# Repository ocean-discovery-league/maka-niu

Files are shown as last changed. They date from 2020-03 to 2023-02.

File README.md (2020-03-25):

# maka-niu

"Maka" - Eye, "Niu" - Coconut

Maka Niu, aka the "CocoCam,"  is a low-cost oceanographic camera and sensor platform that enables the exploration of undersea environments using a new pressure-tolerant camera housing and an all-natural, locally sourced, biodegradable buoyancy-control device. The coconut (Cocos nucifera ) can float for over 3,000 miles and still remain viable; as such, it makes an excellent organic platform for deploying scientific apparatus.

Maka Niu is a community-driven project that allows local groups to explore and monitor their marine resources. Based around off-the-shelf single-board computers and readily available microprocessors, Maka Niu is inexpensive to produce, easy to program, and simple to use. Designed as an open platform for scientific education and exploration, it will give classrooms and communities the ability to upload video and sensor data into FathomNet, a centralized database where machine learning algorithms assist with classification of marine species, seabed substrate identification, and accumulated time-series sensor data. This data will be publically available, allowing visualization, sharing, and discussion with policy makers from the local to global levels.

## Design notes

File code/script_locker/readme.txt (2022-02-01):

The scripts in this folder need to be copied to the following destinations if those files are outdated. 
This would be the case for fresh operating systems, or if the scripts them selves are revised.

Use sudo cp to get to replace the following files:

(to setup auto start of the main python script along with error dumping)
/etc/rc.local

(to avoid leftover flags from boxing)
/var/www/html/macros/startstopX.sh

(To enable ic2 and spi)
/boot/config.txt

(To give python control of image and video filenames) 
/var/www/html/raspimjpeg

(With new pi zero 2 w, to library error when running python script)
/usr/local/lib/python3.7/dist-packages/adafruit_platformdetect/constants/boards.py

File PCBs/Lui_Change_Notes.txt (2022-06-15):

The CHG pin and the CHEM pin on LTC4007 should be connected to ground to disable timer termination, and to set final charge voltage at 4.1V to avoid OV states. 

BMS
Observations:
-still will cut off charging as it get a little too hot. 
-for a test, TH2 replaced with 10K resistor. This does prevent the heat trighgered stop, but it's probably not something we want unltimately. 
TH2 put back. 
-Root issues is L2 and L3 get too hot. Should study up on inductor efficiency to reduce waste and improve heat dissipation in the PCB with vias and copper planes etc.
-There was confusion about the hall sensing. It all works when the pi and hall are connected together. 
-I think the fact that the pi provides ground to the hall sensor was a bad design choice, but I was short on wires I could use.
-R25 was not soldred properly, fixed and output is now stable off, till cool, and then back on, during overheat shutdown situation. 
-But this temp power loss is not ok if usign wireless charging, only ok with direct power supply. 
-

Changes:
-Cut the SHUT_DOWN_SIG line at the charger IC. It does not pull the line high when charging is not in effect( Should add resistor option to pull up this signal)
-Current limiting resistor set at 0.200ohm, limiting the 15V line to half amp. That measn the 12V line is .625ams, for a charging system running at 7.5W. Sadly this is half of original intent.
-Should improve thermal dissipation.
-Can increase PCB size and cover up all the screw holes. Slighly annoying for assembly, but heat management is more important.
-Make sure R25 is assembled. 
-Cut the TS_EOC line, believing that it was interfering with charging. Does not appear to be the cause
-Looking at scope, connection made and then instanly lost. Perhaps cause is inrush current at the boost circuit. Therefore, changing the inrush controlling cap on the BMS. Much imroved but not perfect. 
-C12 changed from 15nF to 1500nf, which should increse statup time from 1125uS to ~100ms (HEADS UP, BMS# 1 and 3 have 0.22uF caps at C12)
-Thermistor on the BMS replaced with 10K resistor. Charging now works longer, until it crashes but now I think the cause is heat from the bms affectign the wireless receiver circuit. 
-Reducer current consumption further by using .300 ohm R_sense. Now can truly a achive continuos charging, expect after 2 hours the charge timer kicks in.
-Disabled charge timer by shorting CHG pin to gnd
-A bit earlier, changing the charging rate current sense resistor to achieve higher final charge voltage, since I cut off power when we reach 10% of max possible. 
-This worked to raise final voltage to 4.15V, but introduced strange behavior that "locked" charging after one attempt. Resistor return to original 0.1 value. How can I get this to work in both situations
-C19 change to 1uF to increase soft start time. 

-Next: reassemble with thermal separator and reduce current by placing 0.250ohm current limiter, reconnect TS_EOC line
-Great, can now charge continuously. Let's run 1 hour semi open, then one hour fully closed.
-REsearch how to reduce heat in the first place. The inductors I used have pretty high resitance, 0.2 ohms, i can get once with quarter that. So I calcualte heat dessipation to be .2W, and I can bring it down to .05W 
-replaced with new inductors. Some imporvement, but not significant
-Test TS_EOC, am not understanding why this does not act as expected. Reached out to Renesas.
-On charger 1, C12 and C19 now 1uF.

-WARNING: Feb2nd 2021: Way too many BMS boards have only one time charge behavior. What gives? Preboost is fine. 

-Total discharge test: ~24 hours with raspidvid running, wifi on
-Total charge enclosed test: 11 hours when current limiting with 0.3ohm, 5V fan cooling
-Total discharge test: 1:45PM, X hours, wifi off, recording 30 minute videos in succesion. Boxing enabled so may prevent some videos. 
-Total charge enclosed test, 5V fan, .25ohm current limit, new thermal pad with higher pressure sandwich, lower height inductors: Started at 2:45PM. end 11:15. Charger current at start is .72amps

CHARGER BOARD
Notices: 
- New board does not flash any LEDS on power up, indicating a major issue
- Fan is started off the bat, indicating TS not behaving as intended. Noteworthy is that the eval board has TH1 unpopulated, so this coudl easily be the entire problem. NOPE, not that.
- 5V, 3.3, and 1.8 Volt lines provided by the chip are all good and clean, indicating chip is powered and at least partially functional. 
- SIGH. This chip is P9242-RBNDGI8 (colloquially P9242-R3 or RB), and it seems we wanted P9242-RNDGI8 aka(but colloquially P9242-R). Pretty dumb 
- Replaced P9242-R. All good!
- The circuit that control the fan uses a compartor and it's making the opposite decision. inputs flipped.
- Cooling fan adjustements: R17 swapped for 12.1Kohm to reduce fan on threshohold. Works but annoying oscilating behavior.
- added 90K ohm hysterisis resistor. Now very happy with performance, but after some time, would recommend even higher value so that the fan eventually shuts off in idling mode. use 250K
- Consider charging fan power source to 5V rather than 12V for quiter operation. Current cooling seems excessive.  

SYSTEM WIDE
next try to limit current of RX board and pump 9W. Yeah, added a 5.1K ohm R at R22 on the RX board, and power transfer does work now, but still cuts out after a few seconds. (currently removed, put it back))
This shoudl work better now if tested with the BMS with it's own current limiting. 
Main issue i think is distance between coils and alignment issues. Fixed alignment with pins, but the coil distance is I think over 3mm so work next step make sure coil distance is 2.5 to 3mm.

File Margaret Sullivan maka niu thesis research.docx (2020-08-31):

Margaret Sullivan

Thesis Document/ Progress Report

LED module for Maka Niu

After meeting, I have identified three separate components of the project.

1. Geometry of the Light
2. Requirements of Light
3. Circuit Design

Geometry of Light

The desired geometry will heavily depend on the use interviews and input. In order to account for that I created a script in MATLAB to visualize different combinations of variables in order to see what the light covers.

The variables in the geometry are the following

• θ the camera lense angle

• α the LED light projection angle

• φ the angle of the led

• x distance from light to camera

Considerations into the geometry include the ideal range of photography and the width of the lights from the camera. These both will depend on the use cases. The following figures display different combinations. The light projection of the LED is based on the Full Width Half. Minimum (FWHM) value. The beam of light is not as definitive as pictured. The distance between the lower and upper FWHM intersection points and the camera are calculated by

Lower Intersection=x tan⁡(90-φ-α/2 )

Upper Intersection=x tan⁡(90-φ+α/2 )

In these figures, the blue outlines are the edge of the FWHM beam. The camera view is shown in-between the red lines.

Without more user input there is no way to choose the optimal lighting situation. Additionally, different usages may contradict each other in terms of optimal lighting geometry. These must be taken into account when deciding the geometry.

Requirements of Light

In order to determine which LEDs to use and design the module the light necessary must be calculated. The light required will depend on many available such as time of day, depth, and distance. To accommodate these changes another MATLAB Script was written to determine the minimum light for various distance.

The minimum light required for a camera is dependent on make and model. To begin we look at the responsivity of the cameras sensor module. Transforming that information into a light requirement per pixel allows for the calculation of light needed at the object of interest to begin.

Factors that affect the light requirement that will be variable

•Distance of the Object ( y_(dist) ) (assuming it is directly in front of camera)

•Distance of the lights from camera ( x )

•Light attenuation Coefficient ( Kd )

•Emissivity of the Object ( ε )

•The Led Projection angle ( α )

Factors that affect the light requirement that are constant

•Active Pixel Count (3280 x 2464)

•Camera Lens Angle (62.2 degrees) ( θ )

•Absolute Sensitivity Threshold (*NEED THIS*)

•Shutter Speed

•Pixel Size

Starting with the absolute sensitivity threshold we can calculate the total lumens needed for any given factor by the following steps. I created a MATLAB script that follows these calculation and results in the lumens required for the light.

1. *Translate the Absolute Sensitivity Threshold into a useable Unit* Preferably into the Lumens needed per pixel using the Shutter Speed, Pixel Size, and Absolute Sensitivity Threshold.

=#[(lm)/(pix)]

2. Using the Lumens needed for pixel account for the attenuation of light from the object to the lens. Where kd is the attenuation coefficient and the y_(dist) is the distance to the object from the light

Lumens From Object [(lm)/(pix) ]=((# (lm)/(pix) ))/(e^((-kd*y_(dist) )))

3. Accounting for the emissivity of object, calculate the lumens needed per pixel.

Lumens at Object [(lm)/(pix) ]=(((lumens from Object) (lm)/(pix) ))/ε

4. Calculate the Lux at the object using the projection of a single pixel at the distance to the object. Assuming that the pixels cover a square distance, calculating the distance of the arc at the objects’ distance and dividing it by active pixels in that direction gives us the projected area.

arc Length [m]=θ/(360°)2πy_(dist)

area per pixel (m^2)/(pix)=((arc Length)/(wide Pixel #))^2

Lux at Object (lm)/(m^2)=(Lumens at Object [(lm)/(pix) ])/((area per pixel)[(m^2)/(pix)])

5. With the lux at object needed known, we can back track using the surface area of the cone of light provided by the LED. To calculate we must know the distance from the light to the object.

Distance from light [m]=√((x)^2 +(y_(dist) )^2)

6. To calculate the surface area of the light provided by the LED at the distance we must calculate the Solid angle.

∫_0^θ 2π(Rsin(ϕ))Rdϕ=2πR^2 ∫_0^θ sin(ϕ)dϕ

solid angle Ω=2πR^2 (1-cos(θ))

Using a unit sphere so R = 1, the solid angle equation reduces to

Ω=2π(1-cos(θ))

Surface Area [m^2 ]= Ω*(Distance from light )^2

7. To calculate the total lumens at the given distance we can use the Surface area of the light (the spherical cap) at the distance and the needed lux.

Lumens ariving at Object [lm]= Surface area [m^2 ]*lux at Object (lm)/(m^2)

8. Accounting for the light attenuation from the LED to the object we are left with the total lumens needed from the light.

Lumens from light [lm]= (Lumensat Object [lm])/(e^((-kd*Distance From Light)))

This calculation should give us an idea of the lowest number of lumens needed to be produced by the LED given the situation.

Some Key Assumptions made

•Light is evenly distributed within the FWHM

•Attenuation equation works for Lumens

•Pixels cover equal area

•Only use the active pixels

•The object is directly in front of camera

To begin the calculations to determine lumens the amount of light per pixel is necessary. There are many ways or estimating/ determining this number, the below steps show the method in which I estimated it. The data sheet is not complete, so researching similar cameras I was able to come up with an estimate for many necessary components. A detailed study was conducted with the use of the IMX249 sensor (https://www.flir.com/discover/iis/machine-vision/how-to-evaluate-camera-sensitivity/) The IMX249 has some key differences from the Raspberry Pi Camera’s IMX219, but it provides useful details. They differ on pixel size, shutter speed, and total active pixels, but use the same CMOS board and should have similar sensitivity.

The IMX249 absolute sensitivity threshold, meaning the signal is equal to the noise of the sensor is at a light density of 1[ photon/μm^2 ] . Additionally, the saturation light density for the IMX249 is 1200 [ photon/μm^2 ] . The IMX249 has a pixel area size 30 times of that of the IMX219. This results in the IM219 absolute sensitivity threshold to be approximately 30 [ photon/μm^2 ] .

(watts)/(pixel)=[photon Density[(photons)/(μm^2)]][energy of photon[J/(photon)]](area of pixel)

Lumens per pixel =((watts)/(pixel))(LED efficiency)

energy per photon =h*c/λ

The energy of the photons were estimated using blue light, the most prominent light in the water. Where λ is the wavelength of blue light, h is planks constant, and c is the speed of light.

Using the steps listed above to reach the absolute minimum threshold, 39 lumen are required at an object distance of 2 meters with a light FWHM angle of 30. This only reaches the lowest boundary of visibility. For a quality photo I estimate we will want 1/3 of the saturation lighting which puts are light density at approximately 1200 [ photon/μm^2 ] . Using the MATLAB script based off the methodology above this lighting density requires 1550 lumens between the two LED modules.

https://www.flir.com/discover/iis/machine-vision/how-to-evaluate-camera-sensitivity/

-all the absolute sensitivity stuff

https://aggressivegarden.com/ppfd/

https://www.lumigrow.com/learning-center/blogs/par-ppf-ppfd-dli-ppe/

https://www.ncbi.nlm.nih.gov/pmc/articles/PMC4354036/

http://electron6.phys.utk.edu/phys250/modules/module%201/photons.htm

https://www.arducam.com/downloads/modules/RaspberryPi_camera/IMX219DS.PDF

imx 219

https://photo.stackexchange.com/questions/21776/what-is-the-lowest-level-of-luminous-flux-a-camera-can-detect

https://photography.tutsplus.com/articles/a-guide-to-using-consumer-led-bulbs-for-photography-and-video--cms-22708

https://www.dormgrow.com/par/

https://www.britannica.com/science/seawater/Optical-properties

https://study.com/academy/lesson/energy-momentum-of-a-photon-equation-calculations.html

https://www.stemmer-imaging.com/en/knowledge-base/sensitivity/

https://en.wikipedia.org/wiki/Solid_angle

https://www.pveducation.org/pvcdrom/properties-of-sunlight/photon-flux

https://www.pveducation.org/pvcdrom/properties-of-sunlight/spectral-irradiance

http://www.parsource.com/content/light-unit-conversion-table

https://support.pixelink.com/support/solutions/articles/3000034837-how-to-interpret-digital-camera-parameters

https://www.nde-ed.org/EducationResources/CommunityCollege/Radiography/Physics/attenuationCoef.htm

https://www.esf.edu/efb/schulz/Limnology/Light.html

https://www.lumenera.com/blog/understanding-camera-sensitivity-a-look-at-the-numbers

https://www.sciencedirect.com/topics/engineering/luminous-intensity

https://www.waterontheweb.org/under/lakeecology/04_light.html

http://cmore.soest.hawaii.edu/summercourse/2013/documents/2013_lectures/Week2/Day1/5_barone_LectureAgouron2013.pdf

https://www.ledsupply.com/leds/cree-xlamp-xm-l2-leds?gclid=CjwKCAjw9vn4BRBaEiwAh0muDIgXzSZ8uIiwv8MGID8M_GXzRxrjX149hkezV1Zndyf2tEIbTEkI-RoCdfIQAvD_BwE

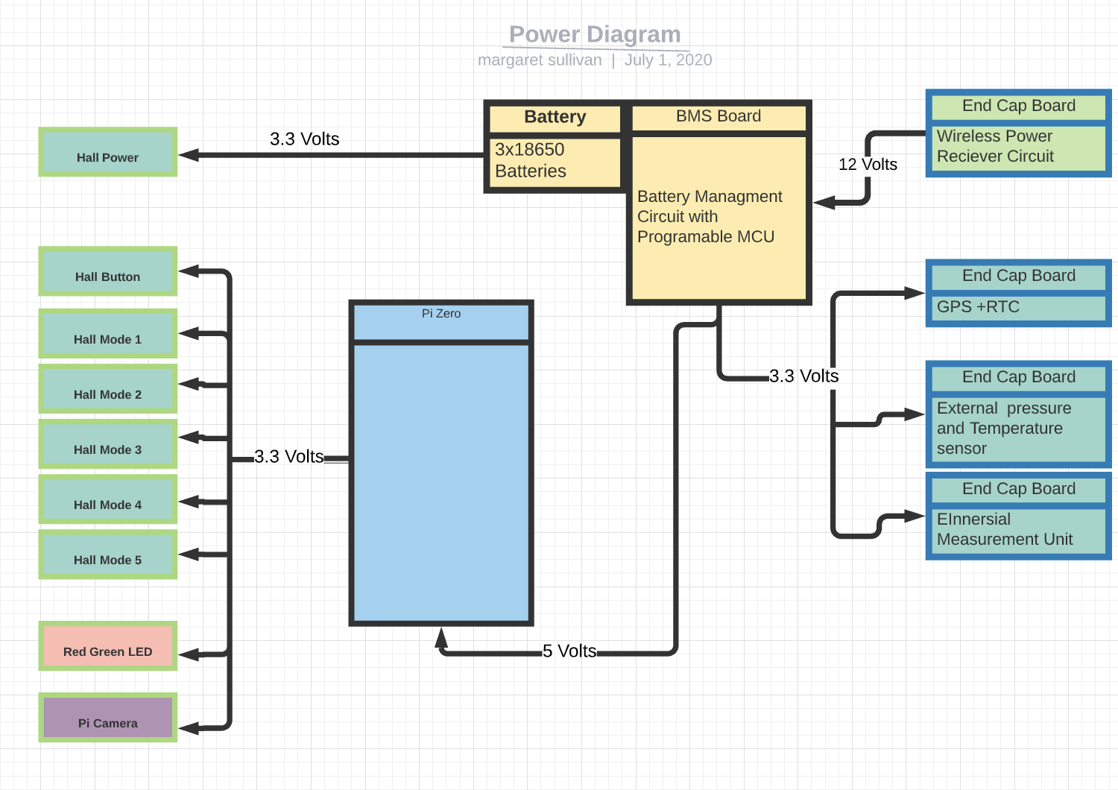
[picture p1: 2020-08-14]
documentation/diagrams/Makaniu Power Distibutiuon Chart.png

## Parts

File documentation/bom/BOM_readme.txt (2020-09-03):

Welcome to the Maka Niu BOM folder
**********************************

For the Maka Niu General Build BOM go to:
https://docs.google.com/spreadsheets/d/1Yi0kvnERcZNjrTwRgHY-_8hGRJwn6BHOZJLXvPHXioU/edit?usp=sharing

For assembly BOMs specific to custom PCBs, got the to pcb project folder 
(ex. PCBs/hall_ring/BOM/)

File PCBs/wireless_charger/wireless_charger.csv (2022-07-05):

Reference | Quantity | Value | Footprint | Datasheet | Digikey | Part Number
C11 C10 | 2 | 22nF | Capacitor_SMD:C_0603_1608Metric | ~ | 311-1370-1-ND | CC0603KRX7R9BB223
C12 C16 C6 C27 | 4 | 1uF | Capacitor_SMD:C_0402_1005Metric | ~ | 311-1697-1-ND | ‎CC0402KRX5R8BB104
C14 C5 C37 C40 C31 C38 C41 C36 C46 C47 | 10 | 10uF | Capacitor_SMD:C_0603_1608Metric | ~ | 490-18214-1-ND | ‎GRM188R61E106KA73D
C15 C4 C21 C13 C26 C34 C1 C29 C30 C33 C3 C2 | 12 | 0.1uF | Capacitor_SMD:C_0402_1005Metric | ~ | 490-10698-1-ND | ‎GRM155R71E104KE14D‎
C17 | 1 | 680pF | Capacitor_SMD:C_0402_1005Metric | ~ | 311-1030-1-ND | ‎CC0402KRX7R9BB681
C18 | 1 | 1nF | Capacitor_SMD:C_0603_1608Metric | ~ | 311-1351-1-ND | ‎CC0402JRX7R9BB102‎
C20 C23 C24 | 3 | 100nF | Capacitor_SMD:C_1206_3216Metric | ~ | 490-16315-1-ND | ‎GRM31C5C2A104JA01L‎
C22 | 1 | 22nF | Capacitor_SMD:C_0402_1005Metric | ~ | 490-6360-1-ND | ‎GRM155R71H223KA12J‎
C25 | 1 | 68nF | Capacitor_SMD:C_1206_3216Metric | ~ | 445-172675-1-ND | ‎C3216C0G2A683J160AC
C28 C32 | 2 | 22uF | Capacitor_SMD:C_1206_3216Metric | ~ | 1276-3047-1-ND | ‎CL31A226KAHNNNE
C35 C39 C19 | 3 | 5.6nF | Capacitor_SMD:C_0603_1608Metric | ~ | 445-180278-1-ND | ‎C1608C0G2A562J080AE‎
C42 | 1 | 0.1uF | Capacitor_SMD:C_0603_1608Metric | ~ | 311-3567-1-ND | ‎CC0603KPX7R9BB104‎
C43 | 1 | 1uF | Capacitor_SMD:C_0603_1608Metric | ~ | 1276-1102-1-ND | ‎CL10A105KA8NNNC
C44 | 1 | 4.7uF | Capacitor_SMD:C_0603_1608Metric | ~ | 490-7203-1-ND | CAP CER 4.7UF 25V X5R 0603
C45 | 1 | 100nF | Capacitor_SMD:C_0603_1608Metric | ~ | 490-14571-1-ND | ‎GRM033R61E104KE14J‎
C48 | 1 | 15pF | Capacitor_SMD:C_0402_1005Metric | ~ | 311-1649-1-ND | ‎CC0402GRNPO9BN150‎
C8 | 1 | 6.8nF | Capacitor_SMD:C_0402_1005Metric | ~ | 490-17758-1-ND | ‎GCM155R71E682KA37D‎
C9 C7 | 2 | 56pF | Capacitor_SMD:C_0402_1005Metric | ~ | 311-3734-1-ND | ‎CC0402FRNPO9BN560
CHG_LED1 | 1 | GREEN | LED_SMD:LED_0603_1608Metric | ~ | 732-4971-1-ND | ‎150060GS75000
D1 D2 | 2 | BAV21W | Diode_SMD:D_SOD-123 | ~ | BAV21W-7-F‎ | ‎BAV21W-7-F‎
D3 | 1 | MBR0530 | Diode_SMD:D_SOD-123 | http://www.mccsemi.com/up_pdf/MBR0520~MBR0580(SOD123).pdf | MBR0530T1GOSCT-ND | ‎MBR0530T1G
FLT_LED1 | 1 | RED | LED_SMD:LED_0603_1608Metric | ~ | 732-4978-1-ND | ‎150060RS75000
Fan_12V1 | 1 | Conn_01x02 | Connector_PinHeader_2.54mm:PinHeader_1x02_P2.54mm_Vertical | ~ | DNP
J1 | 1 | Barrel_Jack_Switch | Custom:CUI_PJ-002AH | ~ | CP-002AH-ND | ‎PJ-002AH
J2 | 1 | Pi_Receiver | Connector_PinHeader_2.54mm:PinHeader_2x03_P2.54mm_Vertical | ~ | S7071-ND | ‎PPTC032LFBN-RC‎
L1 | 1 | 4.7uH | Inductor_SMD:L_0603_1608Metric | ~ | 490-12065-1-ND | ‎LQM18PN4R7MFR
L2 | 1 | 4.7uH | Inductor_SMD:L_1008_2520Metric | ~ | 490-10651-1-ND | ‎DFE252012P-4R7M=P2‎
LX1 LX2 | 2 | MountingHole_Pad | TestPoint:TestPoint_THTPad_D1.5mm_Drill0.7mm | ~ | DNP
Q4 Q1 Q3 Q2 | 4 | DMG7430LFG | Custom:TRANS_DMP3017SFGQ-7_b | ~ | DMG7430LFG-7‎ | ‎DMG7430LFG-7
Q6 | 1 | SIA449DJ | Package_TO_SOT_SMD:Vishay_PowerPAK_SC70-6L_Single | http://www.vishay.com/docs/62864/sia453edj.pdf | SIA449DJ-T1-GE3CT-ND | ‎SIA449DJ-T1-GE3‎
Q7 Q5 Q8 | 3 | 2N7002 | Package_TO_SOT_SMD:SOT-23 | https://www.fairchildsemi.com/datasheets/2N/2N7002.pdf | 2N7002KT1GOSCT-ND | ‎2N7002KT1G
Q9 | 1 | NTR4003N | Package_TO_SOT_SMD:SOT-23 | ~ | NTR4003NT1GOSCT-ND | ‎NTR4003NT1G
R11 R35 | 2 | 200K | Resistor_SMD:R_0603_1608Metric | ~ | 311-200KHRCT-ND | ‎RC0603FR-07200KL
R12 R10 | 2 | 390K | Resistor_SMD:R_0603_1608Metric | ~ | P390KGCT-ND | ‎ERJ-3GEYJ394V‎
R14 | 1 | 2.4K | Resistor_SMD:R_0402_1005Metric | ~ | P2.4KJCT-ND | ‎ERJ-2GEJ242X
R15 R21 | 2 | 10 | Resistor_SMD:R_0402_1005Metric | ~ | P10.0LCT-ND | ‎ERJ-2RKF10R0X
R17 | 1 | 17.8K | Resistor_SMD:R_0402_1005Metric | ~ | YAG3012CT-ND | ‎RC0402FR-0717K8L
R18 | 1 | 0.02 | Resistor_SMD:R_0805_2012Metric | ~ | WSLA-.02CT-ND | ‎WSL0805R0200FEA‎
R29 R28 R27 R25 | 4 | 12 | Resistor_SMD:R_0402_1005Metric | ~ | P12JCT-ND | ‎ERJ-2GEJ120X
R30 R31 R8 R32 R26 | 5 | 100K | Resistor_SMD:R_0402_1005Metric | ~ | P100KJCT-ND | ‎ERJ-2GEJ104X
R33 | 1 | 3 | Resistor_SMD:R_0805_2012Metric | ~ | 311-3.00CRCT-ND | ‎RC0805FR-073RL
R34 | 1 | 100K | Resistor_SMD:R_0603_1608Metric | ~ | P100KHCT-ND | ‎ERJ-3EKF1003V
R36 R37 | 2 | 0.1 | Resistor_SMD:R_0402_1005Metric | ~ | P17359CT-ND | ‎ERJ-2BSJR10X‎
R4 | 1 | 680 | Resistor_SMD:R_0402_1005Metric | ~ | 311-680JRCT-ND | ‎RC0402JR-07680RL
R40 | 1 | 14.3K | Resistor_SMD:R_0402_1005Metric | ~ | 311-14.3KHRCT-ND | ‎RC0603FR-0714K3L
R44 | 1 | 15.8K | Resistor_SMD:R_0402_1005Metric | ~ | 311-15.8KHRCT-ND | ‎RC0603FR-0715K8L‎
R45 | 1 | 220 | Resistor_SMD:R_0805_2012Metric | ~ | 311-220FRCT-ND | ‎RC1206FR-07220RL
R48 R43 R20 R42 R41 R23 R6 R13 R16 R5 R2 R19 R22 | 13 | 10K | Resistor_SMD:R_0402_1005Metric | ~ | 311-10.0KLRCT-ND | ‎RC0402FR-0710KL
R7 R3 R1 R9 | 4 | 1K | Resistor_SMD:R_0402_1005Metric | ~ | 311-1.0KJRCT-ND | ‎RC0402JR-071KL
TH1 | 1 | 10K Thermistor | Resistor_SMD:R_0805_2012Metric | ~ | 478-NB12K00103KBBCT-ND | ‎NB12K00103KBB
U1 | 1 | P9242-R | Custom:QFN40P600X600X100-49N | WPC 1.2.2 Compliant, Wireless Charging Transmitter for 15W Applications |  | P9242-R
U2 | 1 | AP63205 | Package_TO_SOT_SMD:TSOT-23-6 |  | AP63205WU-7DICT-ND | ‎AP63205WU-7
U3 | 1 | LMV331 | Package_TO_SOT_SMD:SOT-23-5 | http://www.ti.com/lit/ds/symlink/lmv331.pdf | 296-6633-1-ND | ‎LMV331IDBVR‎

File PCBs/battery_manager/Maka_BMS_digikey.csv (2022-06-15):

Reference | Quantity | Value | Footprint | Datasheet | Digikey | LCSC | RemQ
0 | 1 | 0 | Custom:TruHole_Batter_Contact_Pad_with_9mm_clear | ~ | 36-240-ND
11.1 | 1 | 11.1 | TestPoint:TestPoint_THTPad_D1.5mm_Drill0.7mm | ~ | ~
12V_OUT1 | 1 | 12V_OUT | TestPoint:TestPoint_THTPad_D1.5mm_Drill0.7mm | ~ | ~
3.4 | 1 | 3.4 | TestPoint:TestPoint_THTPad_D1.5mm_Drill0.7mm | ~ | ~
7.4_1 7.4_2 | 2 | 7.4 | Custom:TruHole_Batter_Contact_Pad_with_9mm_clear | ~ | 36-241-ND
C10 | 1 | 1nF | Capacitor_SMD:C_0402_1005Metric | ~ | 478-1101-2-ND | C1523 | 0
C14 C25 | 2 | 4.7uF | Capacitor_SMD:C_0603_1608Metric | ~ | 1276-1900-1-ND
C16 C15 C1 C7 C11 | 5 | 10uF | Capacitor_SMD:C_0603_1608Metric | ~ | 490-7202-1-ND | C96446 | 3
C17 | 1 | 0.47uF | Capacitor_SMD:C_0402_1005Metric | ~ | 490-12269-1-ND | C47339 | 0
C19 C8 C9 C6 C12 C24 | 6 | 1uF | Capacitor_SMD:C_0402_1005Metric | ~ | 490-10017-1-ND | C52923 | 0
C20 | 1 | 15nF | Capacitor_SMD:C_0402_1005Metric | ~ | 311-1713-1-ND
C21 | 1 | 4.7nF | Capacitor_SMD:C_0402_1005Metric | ~ | 311-1039-1-ND | C1538 | 0
C23 C22 | 2 | 22uF | Capacitor_SMD:C_0603_1608Metric | ~ | 1276-7076-1-ND
C5 C3 C2 C4 C13 C18 | 6 | 0.1uF | Capacitor_SMD:C_0402_1005Metric | ~ | 732-7495-1-ND | C155422 | 3
D2 D1 | 2 | 30V 5A | Diode_SMD:D_SMA | ~ | SK56A-LTPMSTR-ND
D3 | 1 | CRS08 | Diode_SMD:D_SOD-123 | ~ | CRS08QMCT-ND
D4 | 1 | 60V 3A | Custom:D_SOD-123EP | ~ | FSV360FPCT-ND
GND_OUT1 | 1 | GND_OUT | TestPoint:TestPoint_THTPad_D1.5mm_Drill0.7mm | ~ | ~
J8 | 1 | SAM16035-ND | Custom:SAMTEC_T1M-10-F-SH-L-K | ~ | SAM11993-ND
J9 | 1 | Molex 087340-1424 | Custom:Molex_87340-1424_B | ~ | 23-0873401424-ND
L1 | 1 | 4.7uH | Inductor_SMD:L_1008_2520Metric | ~ | 490-10651-1-ND
L3 L2 | 2 | 10uH | Custom:MPL-SE6040-100 | ~ | 1589-MPL-SE6040-100CT-ND
Q3 Q2 Q6 Q1 | 4 | FDC645N | Custom:SOT-23-6_mosfet | ~ | FDC645NCT-ND
Q4 Q5 | 2 | Si3483CDV | Custom:SOT-23-6_mosfet | ~ | SI3483CDV-T1-GE3CT-ND
R10 R15 TH1 R17 TH2 R32 | 6 | 10K | Resistor_SMD:R_0402_1005Metric | ~ | 311-10.0KLRCT-ND | C25744 | 2
R12 R11 R14 | 3 | 1M | Resistor_SMD:R_0402_1005Metric | ~ | 311-1.00MLRCT-ND | C26083 | 2
R16 R23 R7 | 3 | 100K | Resistor_SMD:R_0402_1005Metric | ~ | 311-100KLRCT-ND | C25741 | 0
R18 | 1 | 470K | Resistor_SMD:R_0402_1005Metric | ~ | 311-470KJRCT-ND
R19 | 1 | 270K | Resistor_SMD:R_0402_1005Metric | ~ | 311-270KJRCT-ND
R20 | 1 | 887K | Resistor_SMD:R_0402_1005Metric | ~ | YAG5696CT-ND
R21 | 1 | 110K | Resistor_SMD:R_0402_1005Metric | ~ | 311-110KLRCT-ND
R22 | 1 | 32.4K | Resistor_SMD:R_0402_1005Metric | ~ | YAG3119CT-ND | C26974 | 0
R24 | 1 | 309K | Resistor_SMD:R_0402_1005Metric | ~ | YAG3108CT-ND | C122546 | 0
R25 | 1 | 6.04K | Resistor_SMD:R_0402_1005Metric | ~ | YAG2293CT-ND | C25913 | 0
R27 R26 | 2 | 3.01K | Resistor_SMD:R_0402_1005Metric | ~ | 311-3.01KLRCT-ND | C25889 | 0
R28 | 1 | 4.99K | Resistor_SMD:R_0402_1005Metric | ~ | YAG1447CT-ND | C25903 | 0
R29 | 1 | 0.25 | Resistor_SMD:R_1206_3216Metric_Pad1.42x1.75mm_HandSolder | ~ | 311-0.25ANCT-ND
R30 | 1 | 26.7K | Resistor_SMD:R_0402_1005Metric | ~ | YAG3081CT-ND | C25876 | 0
R31 | 1 | 0.1 | Resistor_SMD:R_1206_3216Metric_Pad1.42x1.75mm_HandSolder | ~ | 311-0.1ANCT-ND | C25334 | 0
R4 R3 R2 R13 R1 R5 R6 | 7 | 1K | Resistor_SMD:R_0402_1005Metric | ~ | YAG1234CT-ND | C11702 | 5
R8 | 1 | 0.02 | Resistor_SMD:R_1206_3216Metric_Pad1.42x1.75mm_HandSolder | ~ | WSLP-.02CT-ND
R9 | 1 | 15K | Resistor_SMD:R_0402_1005Metric | ~ | 311-15.0KLRTR-ND | C25756 | 0
U1 | 1 | AP63205 | Package_TO_SOT_SMD:TSOT-23-6 |  | AP63205WU-7DICT-ND
U2 U7 | 2 | TPS70933DBV | Package_TO_SOT_SMD:SOT-23-5 |  | 296-35483-1-ND
U3 | 1 | BQ77915 | Package_SO:TSSOP-24_4.4x7.8mm_P0.65mm |  | 296-50995-1-ND
U4 | 1 | LTC6994xS6-1 | Package_TO_SOT_SMD:TSOT-23-6 | https://www.analog.com/media/en/technical-documentation/data-sheets/699412fb.pdf | LTC6994CS6-1#TRMPBFCT-ND
U5 | 1 | LTC4007 | Package_SO:SSOP-24_3.9x8.7mm_P0.635mm | https://www.analog.com/media/en/technical-documentation/data-sheets/4007fc.pdf | LTC4007EGN#PBF-ND
U6 | 1 | MP3213 | Package_SO:MSOP-8-1EP_3x3mm_P0.65mm_EP1.95x2.15mm |  | 1589-1626-1-ND

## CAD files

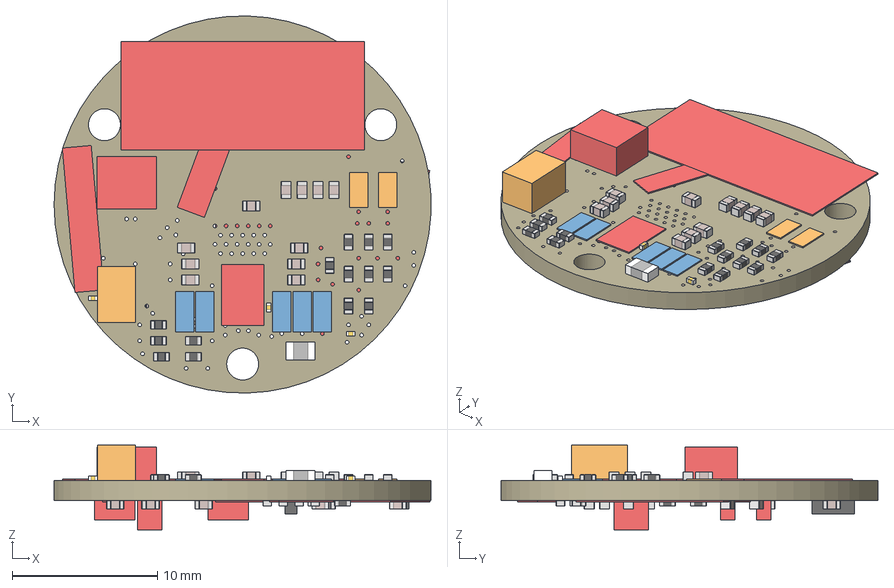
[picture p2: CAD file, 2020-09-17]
PCBs/endcap/Maka Niu Endcap.step
26.0 x 26.0 x 5.85 mm
Board
MOLEX_87759_1450
1nF x 19
10uF x 5
0.1uF x 3
0.5A/40V/420mV
33nH/±5%/500mA x 2
U.FL
KELLER_BREAKOUT
GPS_PROG
20V/0.2A/8MHz/1.2Ω/1Vth x 2
NP x 23
10k x 2
THERMISTOR-2,5
CHARGING_COIL
P9221-R03MM_PAD
XM1110 GPS
ICM-20948
1.8V/100mA

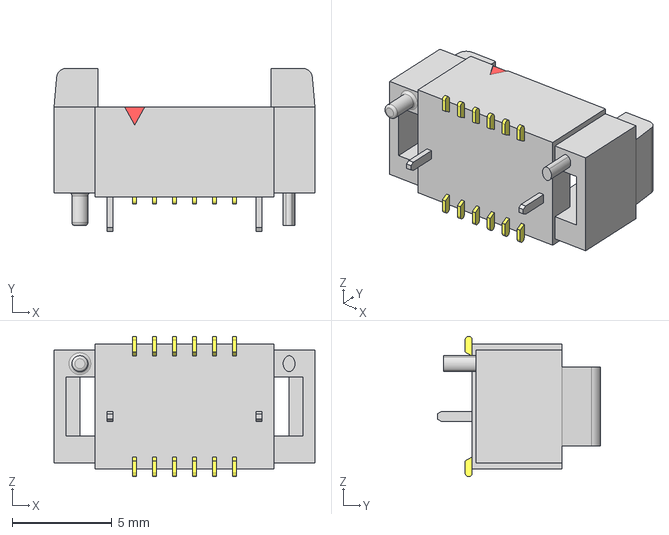
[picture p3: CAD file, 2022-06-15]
PCBs/hall_ring_V2/T1M-06-X-DV.step
13.1 x 8.20 x 7.05 mm
_T1T1M-06-T-DV
_P2T1M-06-T-DV

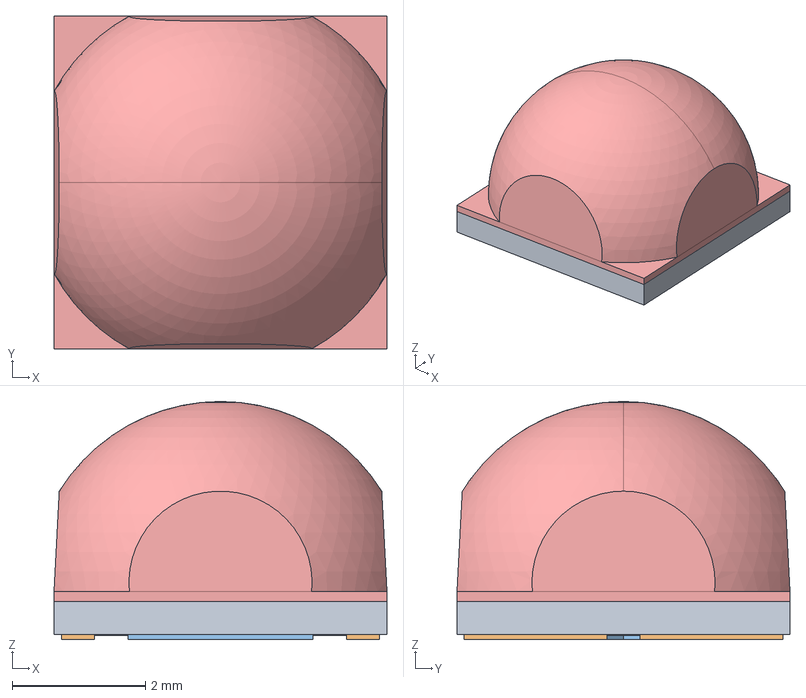
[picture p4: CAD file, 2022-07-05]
PCBs/LED_board/LED_board/XHP50.stp
5.00 x 5.00 x 3.58 mm
2500-00513-CERAMIC
2500-00513-BOTTOM-TRACE
2500-00513-SOLDERMASK-NONOTCH
2500-00513-SOLDERMASK-BACK
2500-00513-TOP-TRACE
2500-00513-TOP-SOLDERMASK
2_85_TRUNCATED_DOME

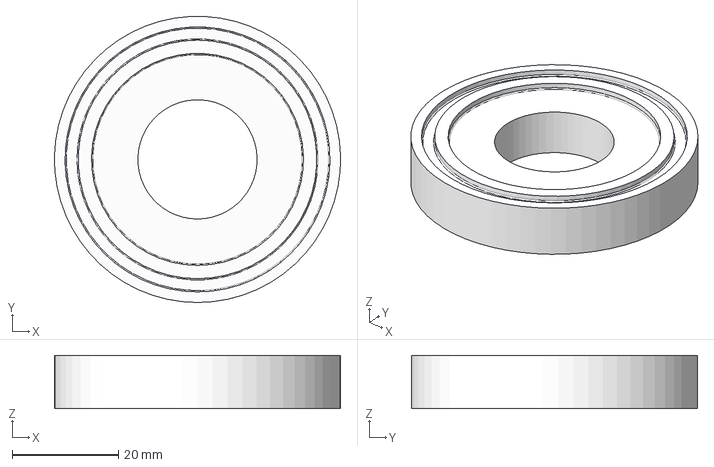
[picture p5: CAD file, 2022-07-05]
PCBs/LED_board_B/LED_Heatsink_1.1.16.step
54.0 x 54.0 x 10.0 mm

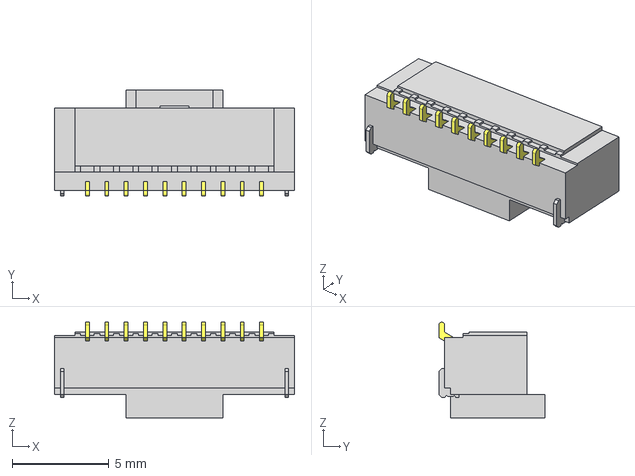
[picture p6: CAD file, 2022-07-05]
PCBs/pi_zero_shield/T1M-10-F-SV-L.stp
12.4 x 5.50 x 4.95 mm
_T1T1M-10-T-SV-L
_P2T1M-10-T-SV-L

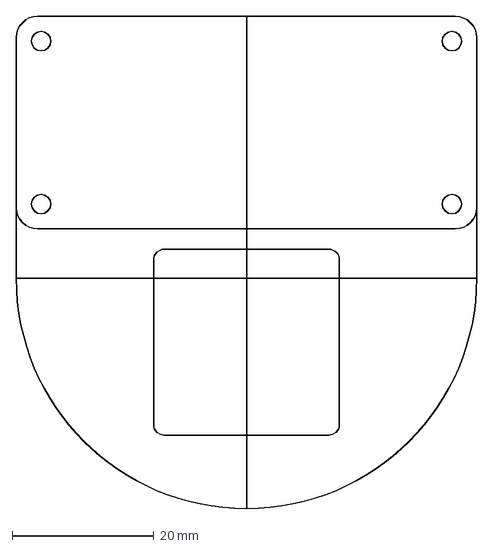
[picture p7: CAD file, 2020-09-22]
PCBs/wireless_charger/charger_outline_large.dxf
65.0 x 69.5 mm

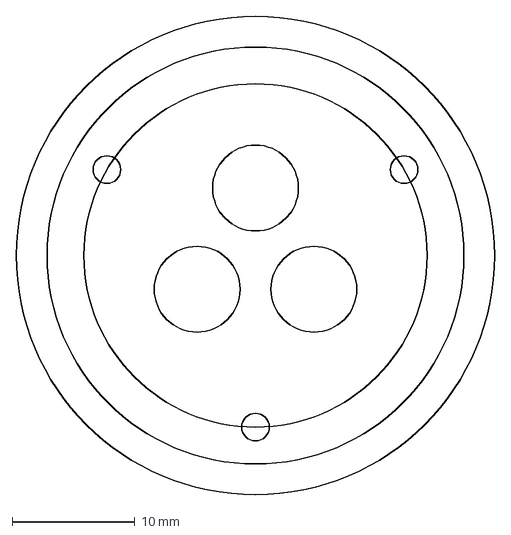
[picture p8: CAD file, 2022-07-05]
PCBs/LED_board/LED_board/LED_board_outline.dxf
39.0 x 39.0 mm

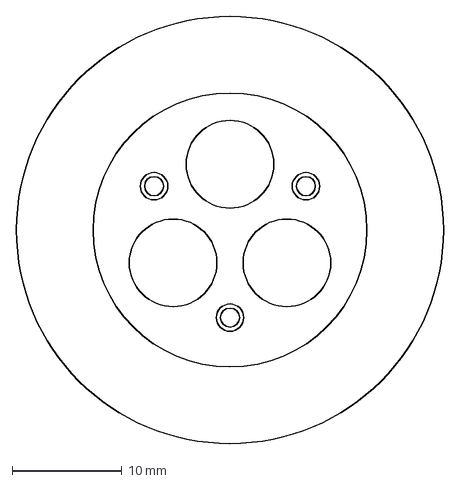
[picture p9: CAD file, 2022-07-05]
PCBs/LED_board/LED_board_outline.dxf
39.0 x 39.0 mm

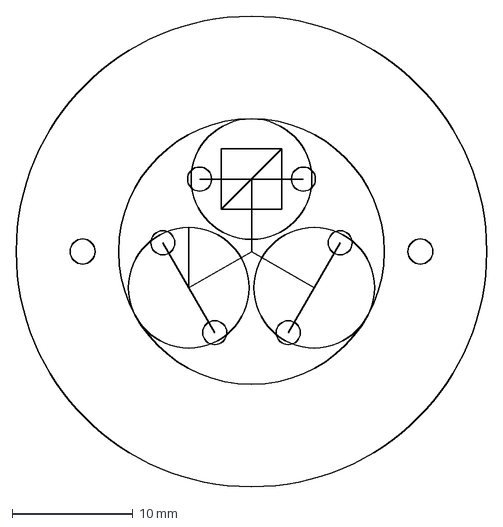
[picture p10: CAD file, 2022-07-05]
PCBs/LED_board_B/LED_board_outline.dxf
39.0 x 39.0 mm

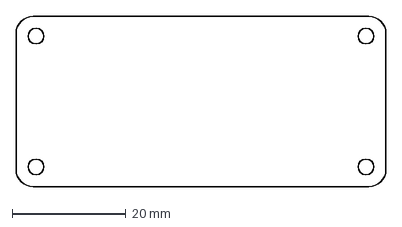
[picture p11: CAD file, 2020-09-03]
PCBs/wireless_charger/charger_outline.dxf
65.0 x 30.0 mm

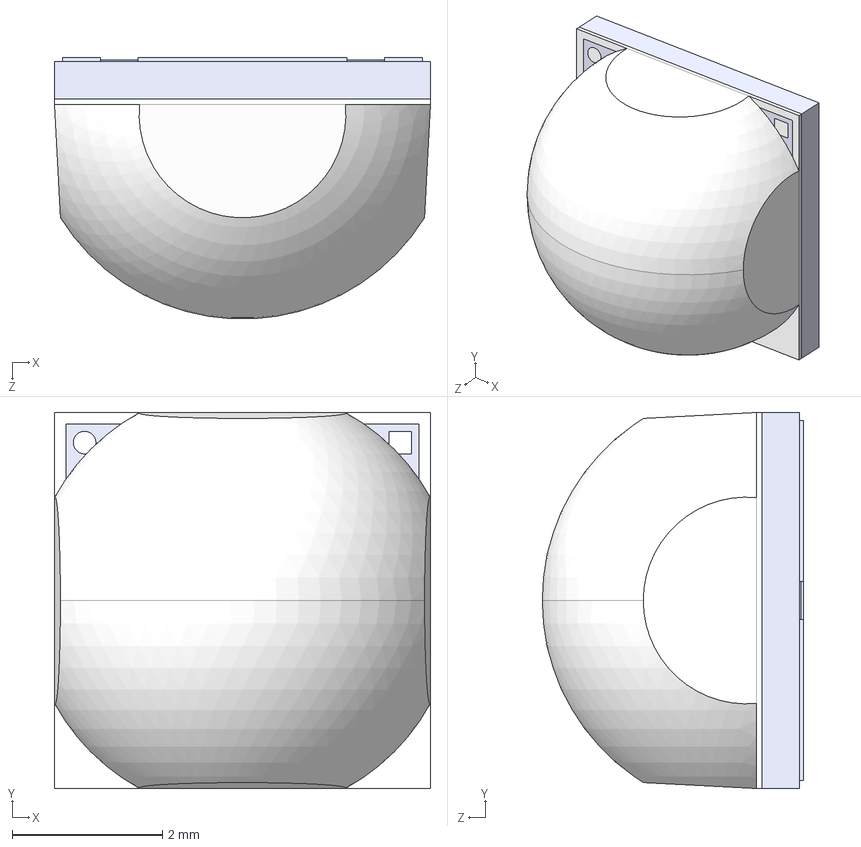
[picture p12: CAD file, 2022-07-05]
PCBs/LED_board_B/Cree LED XLamp XHP50.2.STEP
5.00 x 5.00 x 3.48 mm
2500-00676-C.stp
2500-00676-BT.stp
2500-00676-SMB.stp
2500-00676-SMB1.stp
2500-00676-TT.stp
2500-00676-TS.stp
2610-00073-DOME.stp

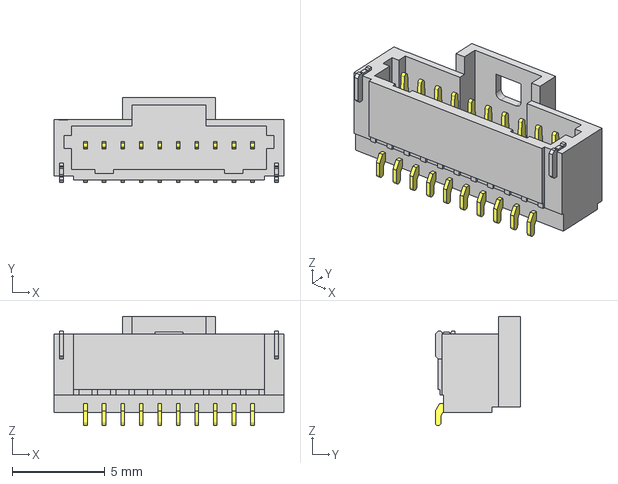
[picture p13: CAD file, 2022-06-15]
PCBs/pi_zero_shield/T1M-10-F-SH-L.stp
12.4 x 4.60 x 5.90 mm
_T1T1M-10-T-SH-L
_P2T1M-10-T-SH-L

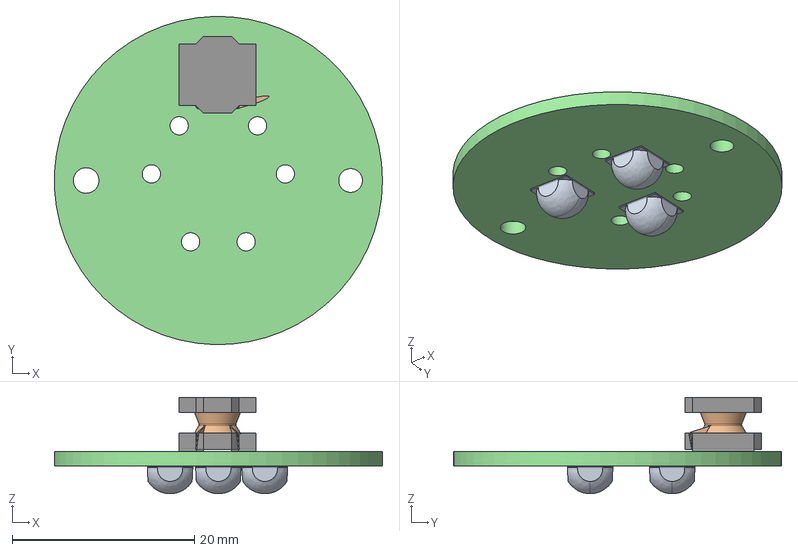
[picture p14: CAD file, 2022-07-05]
PCBs/LED_board_B/LED_board.step
36.0 x 36.0 x 10.6 mm
LED_board PCB

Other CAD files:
PCBs/battery_manager_V1.1/T1M-10-F-SV-L.stp
PCBs/pi_zero_shield/T1M-06-GF-DH.step
PCBs/pi_zero_shield/T1M-06-GF-DH.stp
PCBs/pi_zero_shield/m20-7812045_asm.stp
PCBs/pi_zero_shield/shield.dxf

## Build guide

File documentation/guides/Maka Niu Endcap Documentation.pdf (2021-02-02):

### Maka-Niu Endcap PCB

The endcap PCB is a 6-layer, 26mm diameter board that handles wireless Qi charging, GPS (including external antenna connector), IMU, and breakouts for the Keller pressure sensor and for an external thermistor to provide temperature-related shutdown capability.

The endcap PCB connects to the other PCBs in the stack via a 14 pin Molex connector.

The wireless charging IC is an IDT P9221-R. The datasheet can be found here: https://www.mouser.com/datasheet/2/464/IDT_P9221-R-Datasheet_DST_20171010-1093280.pdf (https://www.mouser.com/datasheet/2/464/IDT_P9221-R-Datasheet_DST_20171010-1093280.pdf)

The GPS module is an AirPrime XM1110. The most recent datasheet must be requested from Sierra Wireless.

The IMU is a TDK InvenSense ICM-20948 9-axis IMU. The datasheet can be found here: https://invensense.tdk.com/wp-content/uploads/2016/06/DS-000189-ICM-20948-v1.3.pdf

Following are the layouts of the top and bottom of the board:

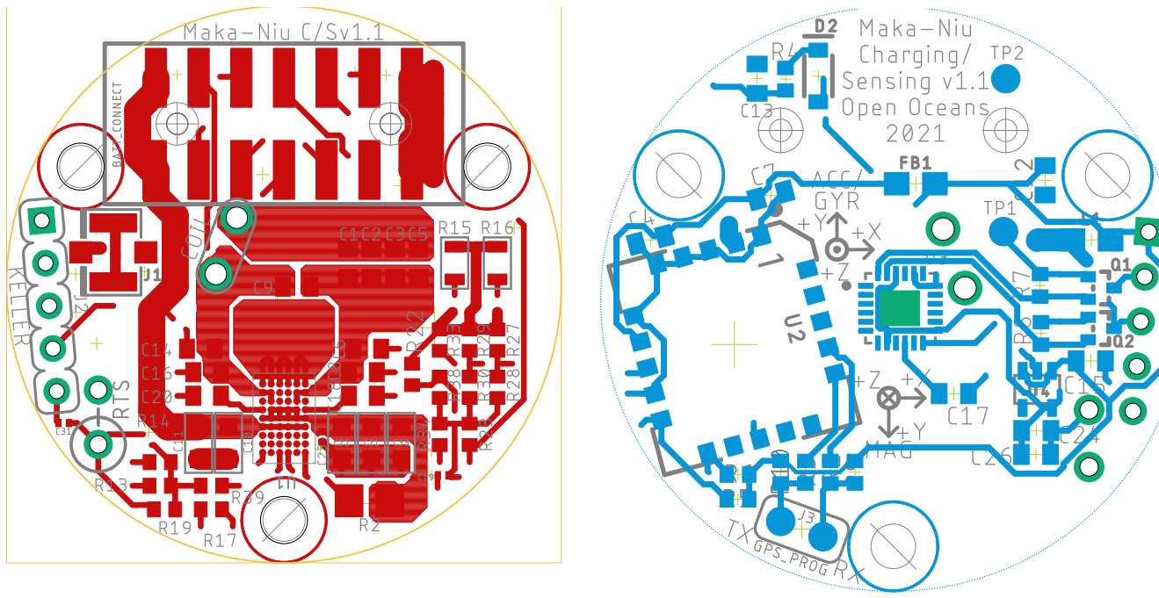
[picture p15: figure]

Top of board, important details

The pinouts for the 14 pin Molex connector are as follows:

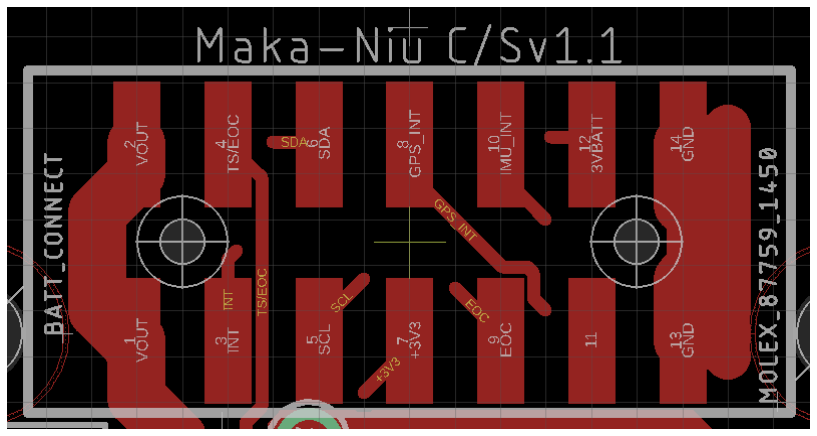
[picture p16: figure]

Pins numbered according to columns left to right and rows bottom to top within columns (as shown in diagram above, viewed in this orientation):

1: VOUT (to main battery)
2: VOUT (to main battery)
3: !INT (for wireless charger)
4: TS/EOC (temperature sensing/end of charge for wireless charger) 5: SCL
6: SDA
7: +3.3V
8: GPS INTERRUPT
9: EOC (from Keller pressure sensor) 10: IMU INTERRUPT
11: unused
12: 3V BACKUP BATTERY (for GPS)
13: GND (common)
14: GND (common)

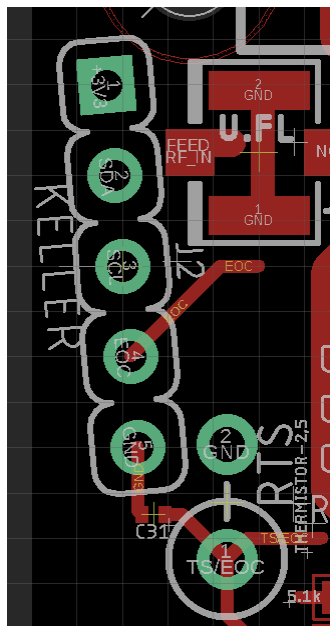
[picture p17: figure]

The pinouts for the Keller pressure sensor and the thermistor are as follows:

For the Keller sensor, where pin 1 has the square pad:

1: +3.3V
2: SDA
3: SCL
4: EOC
5: GND

For the thermistor, where pin 1 is circled:

1: TS/EOC
2: GND

Here is the ECAD layout of the full top of the board:

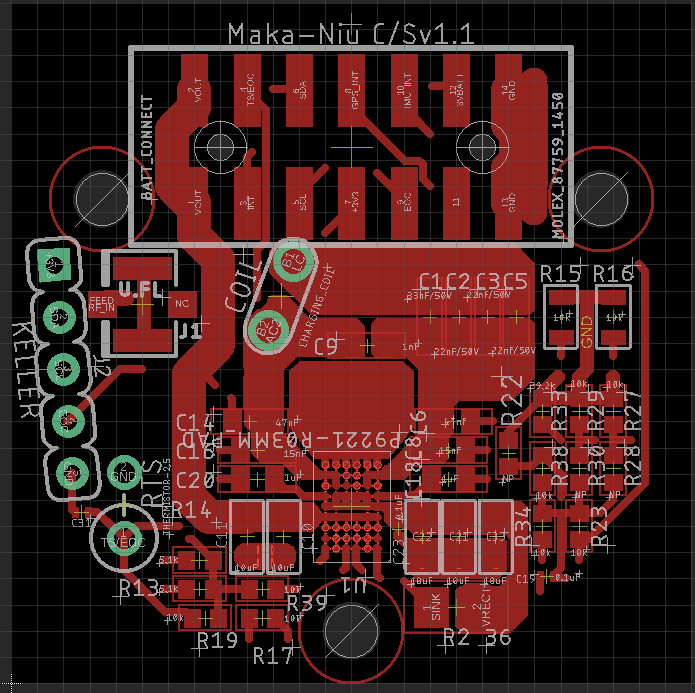
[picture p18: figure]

Important programming resistors to note in the resistor cluster to the bottom right:

R22: used as part of a resistor divider for setting the overcurrent limit (ILIM)
R28: used as part of a resistor divider for tuning foreign object detection (FOD); tunes received packet power gain (RPPG)
R30: used as part of a resistor divider for tuning foreign object detection (FOD); tunes received packet power offset (RPPO)

These resistors are unpopulated in the initial assembly.

Here is a photograph of the prototype assembly. The unpopulated resistors are visible in the lower right, although they are not labeled on the silkscreen. They will be labeled in the final production run.

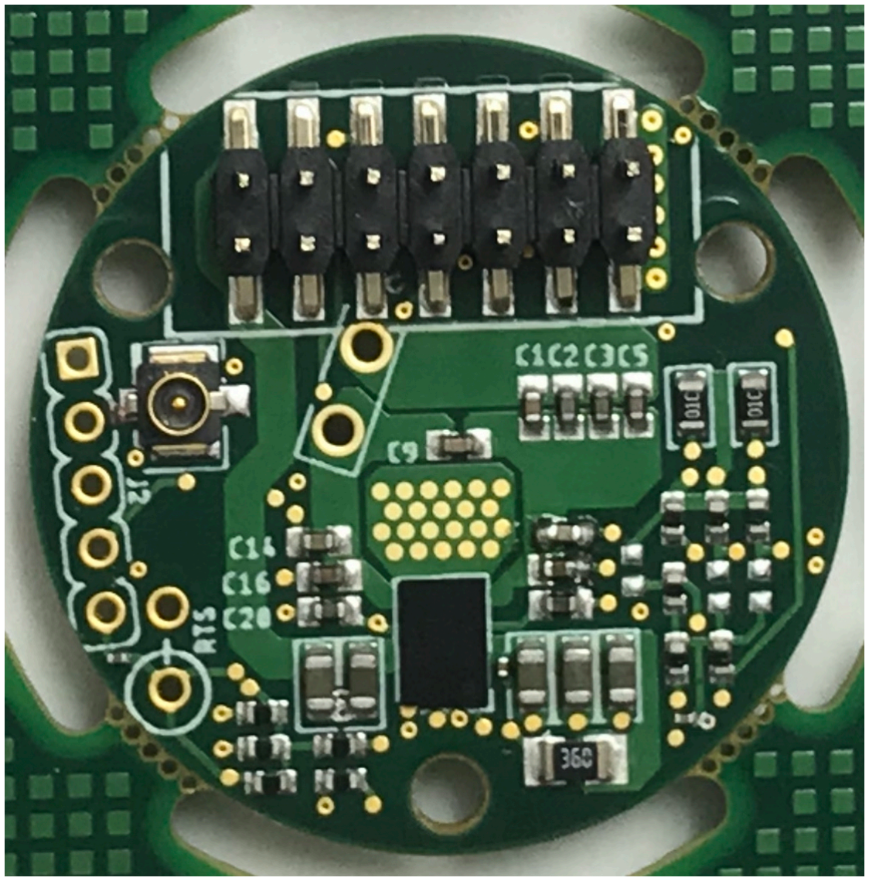
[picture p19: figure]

Bottom of board, important details

The bottom of the board contains the GPS module and the IMU. The important features for manual adjustment/testing are J3, the GPS programming connector, and the two electrical testpoints TP1 and TP2.

Here is the ECAD layout of the bottom of the board:

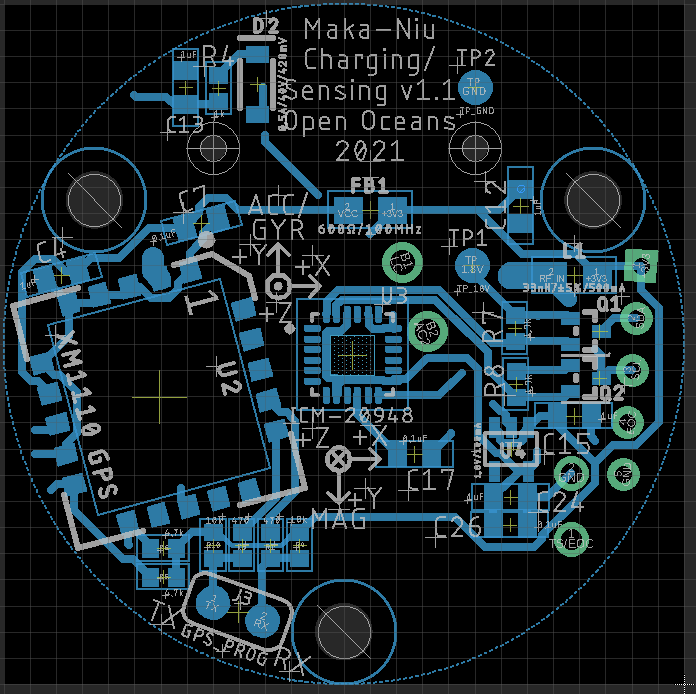
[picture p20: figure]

As can be seen from this image, J3 has TX on the left and RX on the right.

The expected testpoint voltages are as follows:

TP1: +1.8V
TP2: GND

Here is a photograph of the prototype assembly. Note that TX and RX are unlabeled in the silkscreen; they will be labeled in the final production run. Note also that the GPS module is 180° rotated from its correct orientation; this photograph was taken before this assembly error was corrected. It will be correctly oriented in the production run.

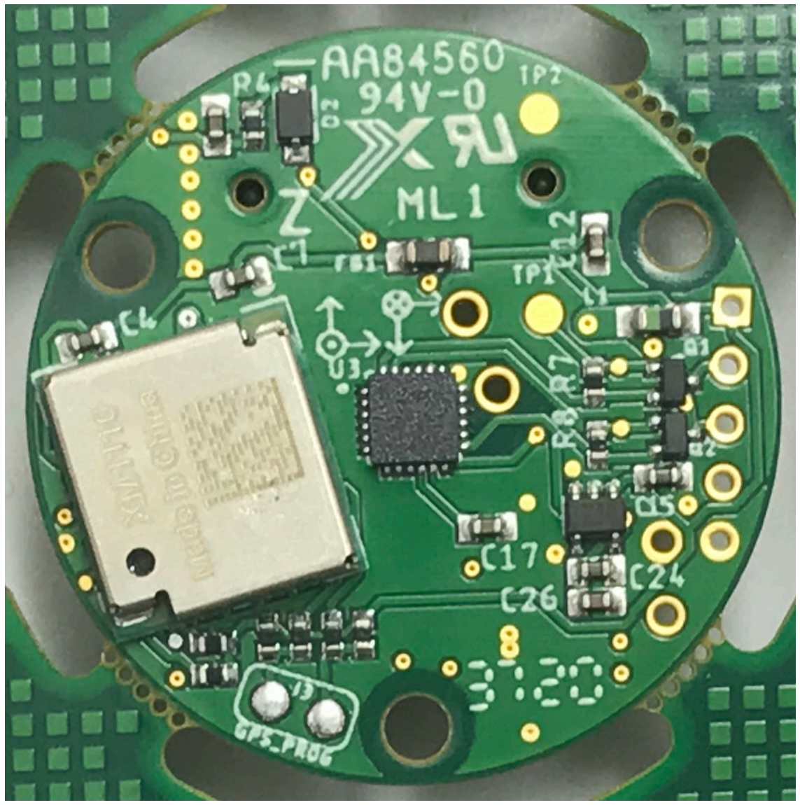
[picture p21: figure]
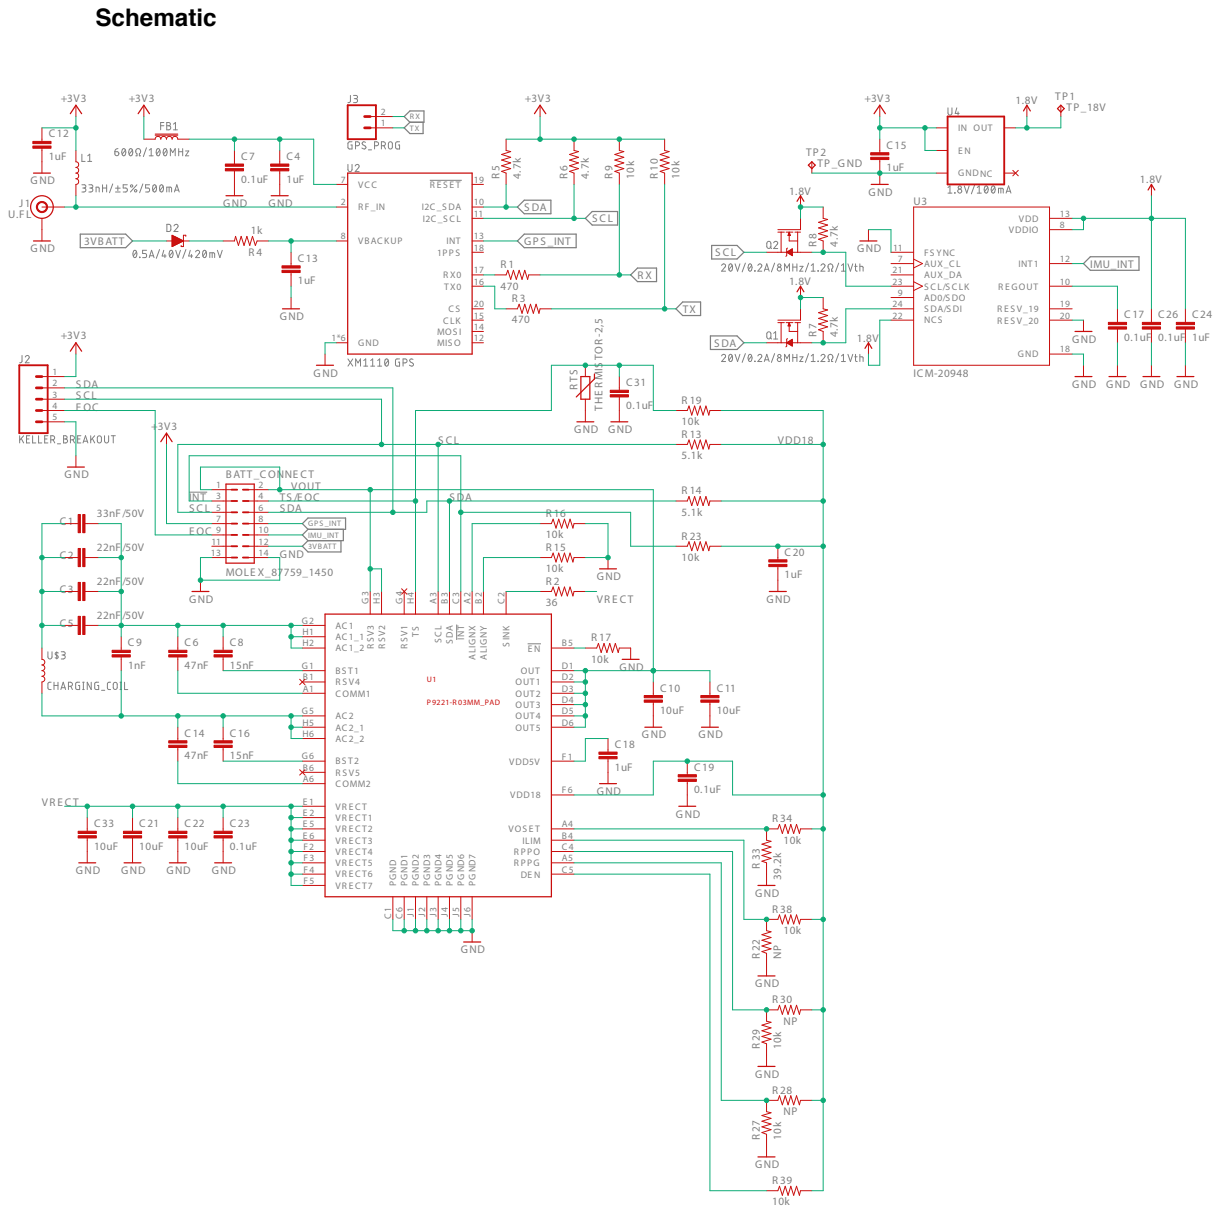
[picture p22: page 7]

GND GND

BS T1 G1 | 10k GND
R S V4 B1 COMM1 A1 | | GND

AC2_1 H5
AC2_2 H6 | GND

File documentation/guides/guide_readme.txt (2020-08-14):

Welcome to the Maka Niu Guide folder
**********************************

For the Maka Niu Build Guide, go to:
https://docs.google.com/document/d/1vic6-aDCgJOBhLbDQZUVHlk4VEvlJy3QFUJLLKdjV5E/edit?usp=sharing

For the Maka Niu User Guide, go to:
______________

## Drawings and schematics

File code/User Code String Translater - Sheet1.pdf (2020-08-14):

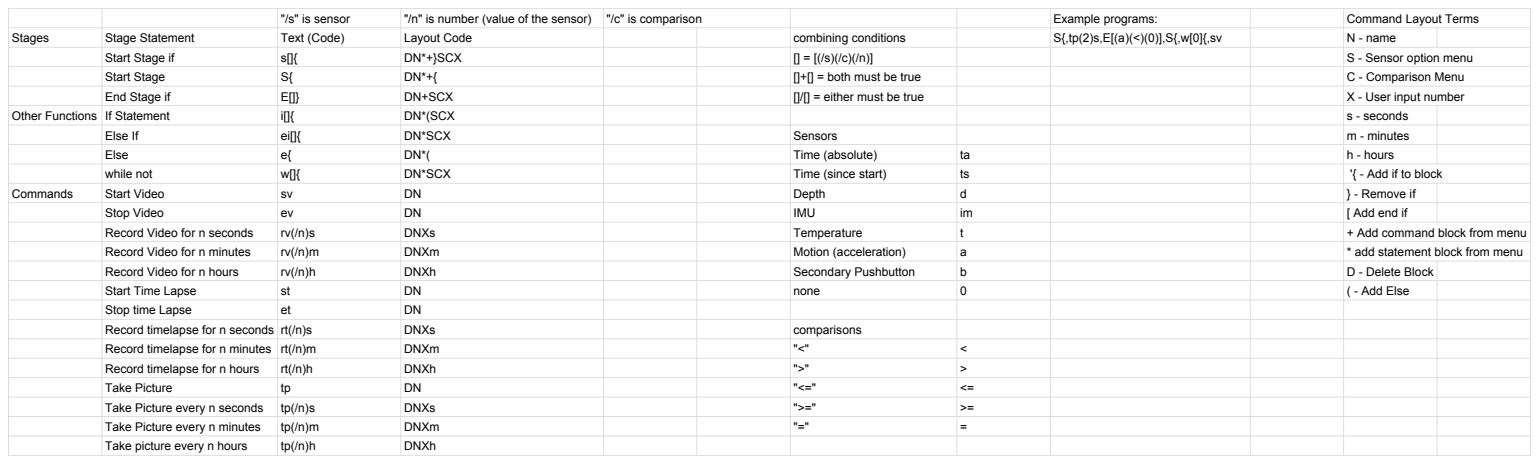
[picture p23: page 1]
"/s" is sensor; "/n" is number (value of the sensor); "/c" is comparison; Example programs:; Command Layout Terms; Stages; Stage Statement; Text (Code); Layout Code; combining conditions; N - name; Start Stage if; DN*+}SCX; S - Sensor option menu; Start Stage; []+[] = both must be true; C - Comparison Menu; End Stage if; DN+SCX; []/[] = either must be true; X - User input number; Other Functions If Statement; DN*(SCX; s - seconds; Else If; DN*SCX; Sensors; m - minutes; Else; Time (absolute)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

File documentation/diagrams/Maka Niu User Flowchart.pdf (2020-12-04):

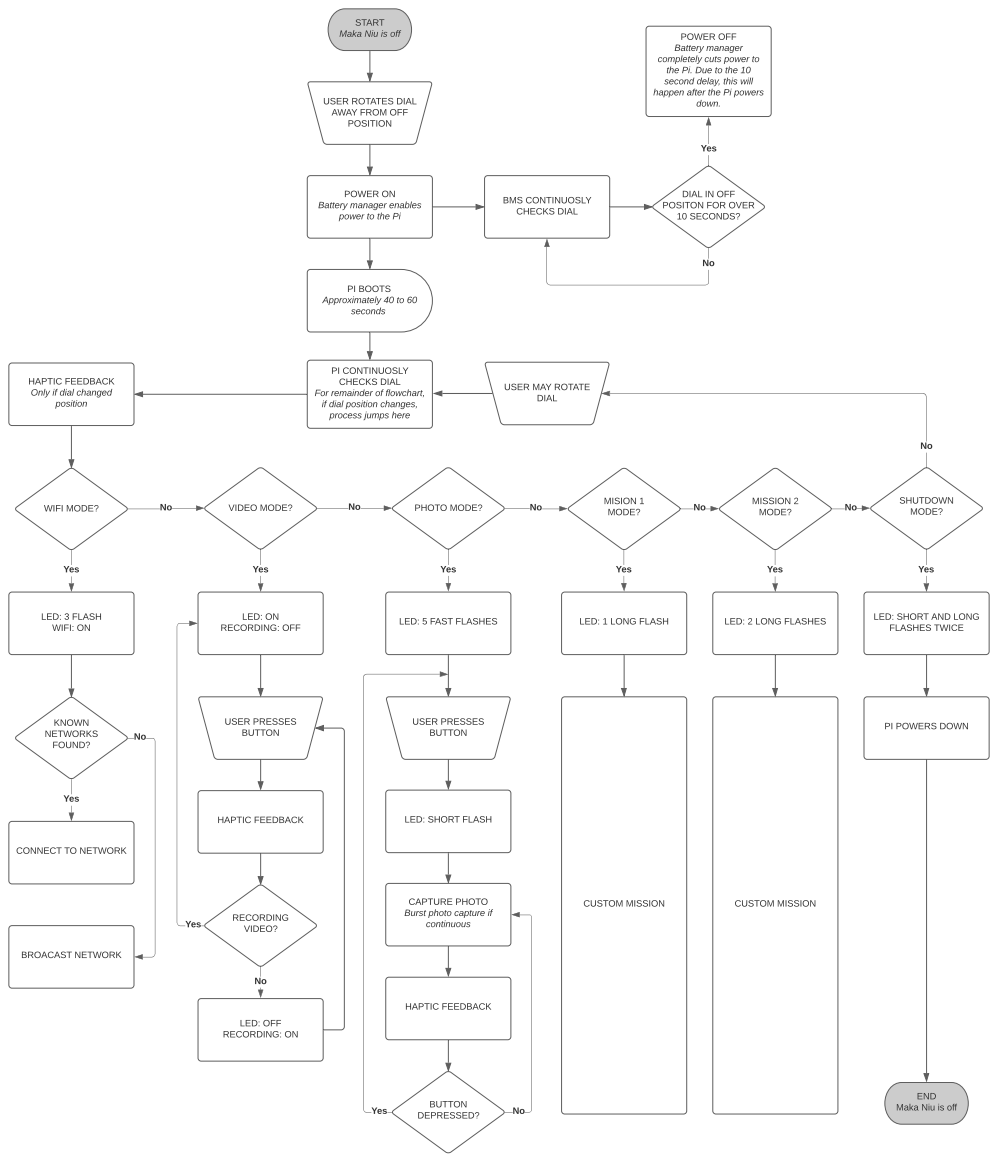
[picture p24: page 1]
BMS CONTINUOSLY CHECKS DIAL; Yes; down.; WIFI MODE?; VIDEO MODE?; PHOTO MODE?; MISION 1; MODE?; MISSION 2; SHUTDOWN; LED: 3 FLASH WIFI: ON; LED: ON RECORDING: OFF; KNOWN NETWORKS FOUND?; BROACAST NETWORK; USER PRESSES BUTTON; HAPTIC FEEDBACK; RECORDING VIDEO?; LED: OFF RECORDING: ON; BUTTON; DEPRESSED? Yes; LED: 1 LONG FLASH; LED: 2 LONG FLASHES; CUSTOM MISSION; PI BOOTS Approximately 40 to 60 seconds

START
Maka Niu is off

POWER OFF
Battery manager
completely cuts power to
the Pi. Due to the 10
second delay, this will
happen after the Pi powers

USER ROTATES DIAL
AWAY FROM OFF
POSITION

POWER ON
Battery manager enables
power to the Pi

DIAL IN OFF
POSITON FOR OVER
10 SECONDS?

PI CONTINUOSLY
CHECKS DIAL
For remainder of flowchart,
if dial position changes,
process jumps here

HAPTIC FEEDBACK
Only if dial changed
position

USER MAY ROTATE
DIAL

LED: SHORT AND LONG
FLASHES TWICE

LED: 5 FAST FLASHES

PI POWERS DOWN

LED: SHORT FLASH

CONNECT TO NETWORK

CAPTURE PHOTO
Burst photo capture if
continuous

END

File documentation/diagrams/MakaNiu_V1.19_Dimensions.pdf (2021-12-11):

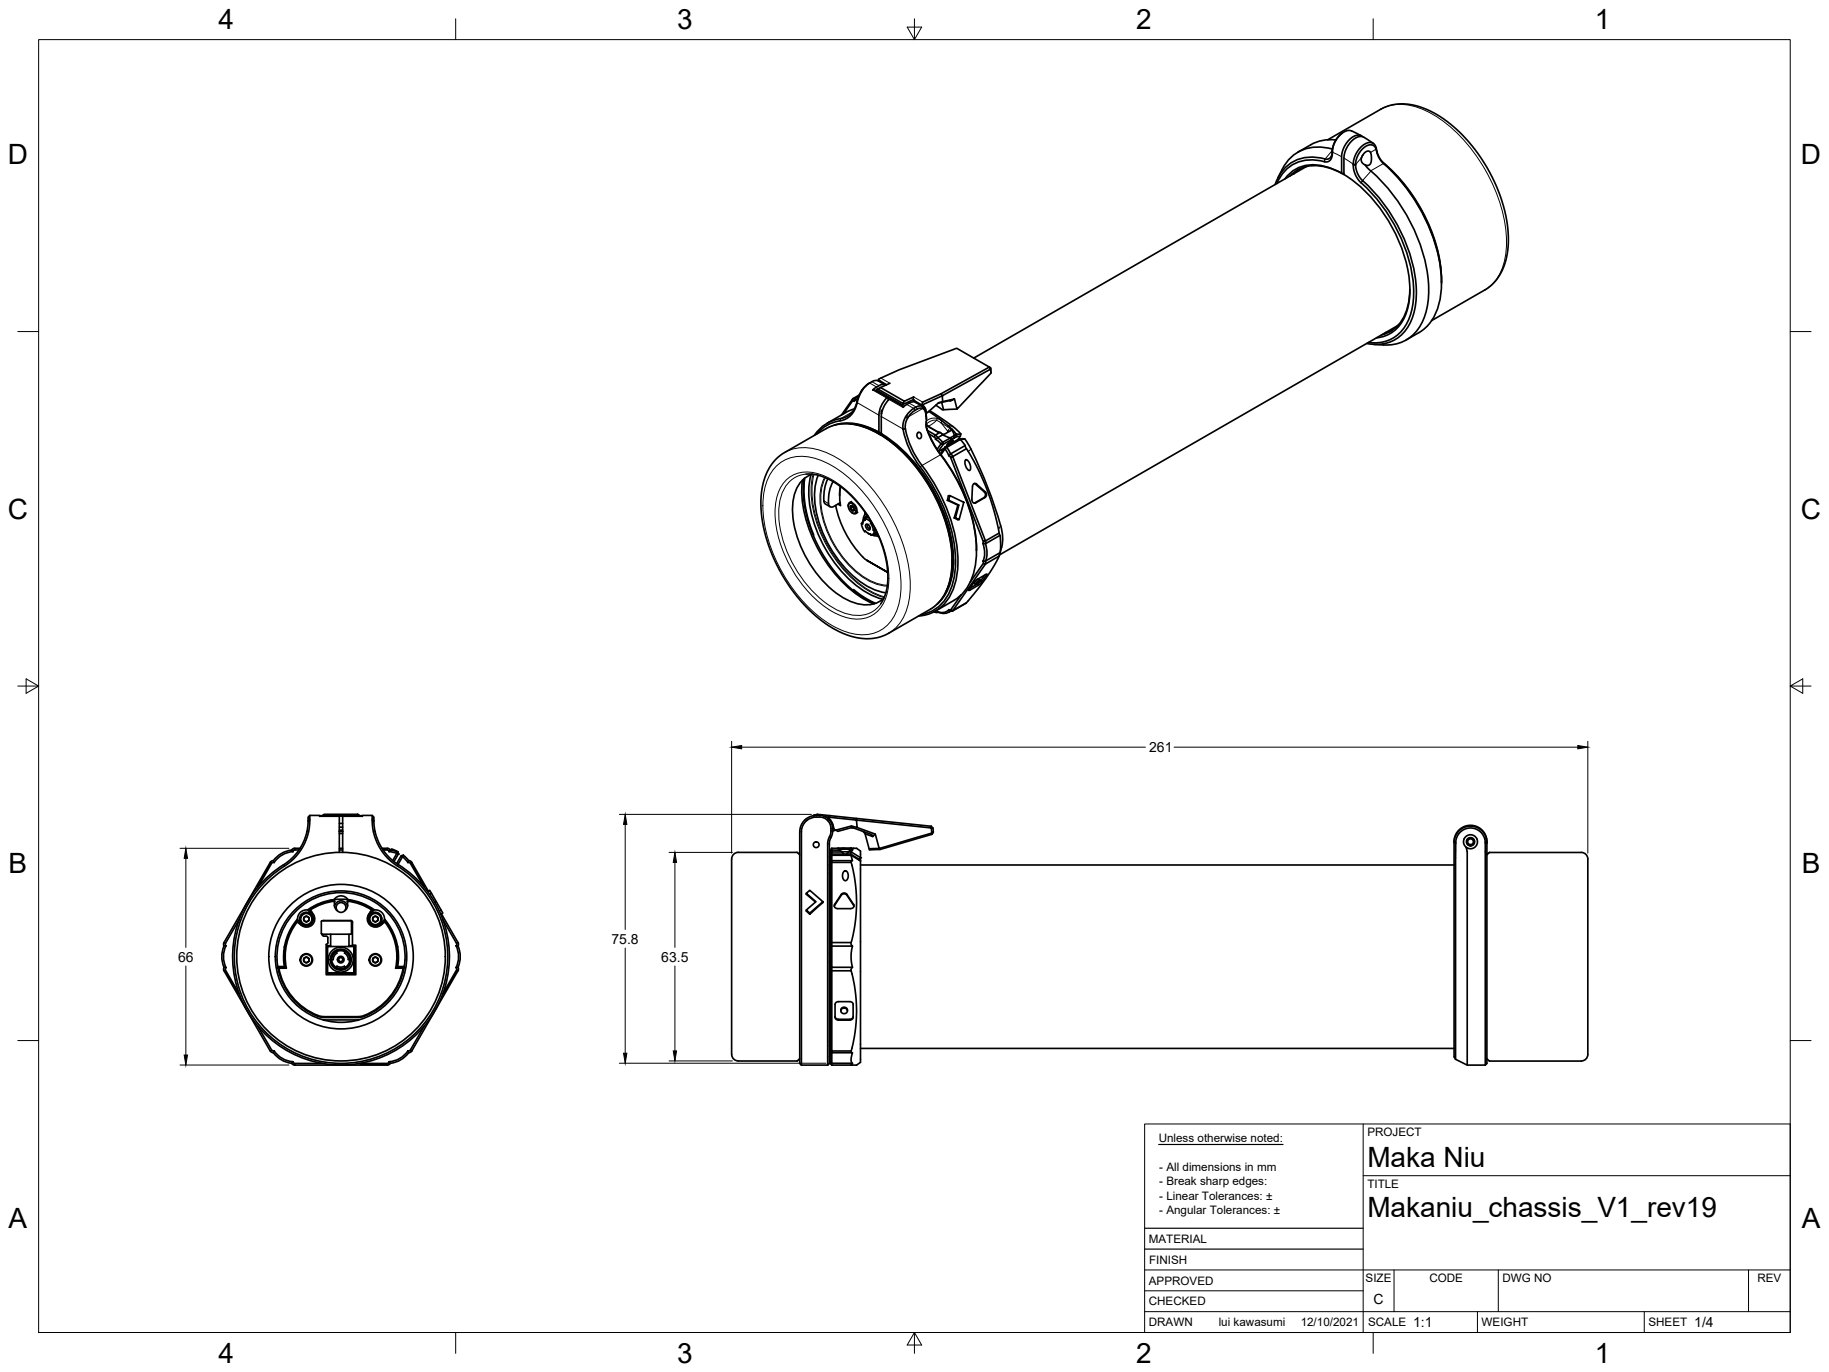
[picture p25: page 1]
SIZE; CODE; DWG NO; REV; lui kawasumi; Maka Niu

Unless otherwise noted:

- All dimensions in mm
- Break sharp edges:
- Linear Tolerances: ±
- Angular Tolerances: ±

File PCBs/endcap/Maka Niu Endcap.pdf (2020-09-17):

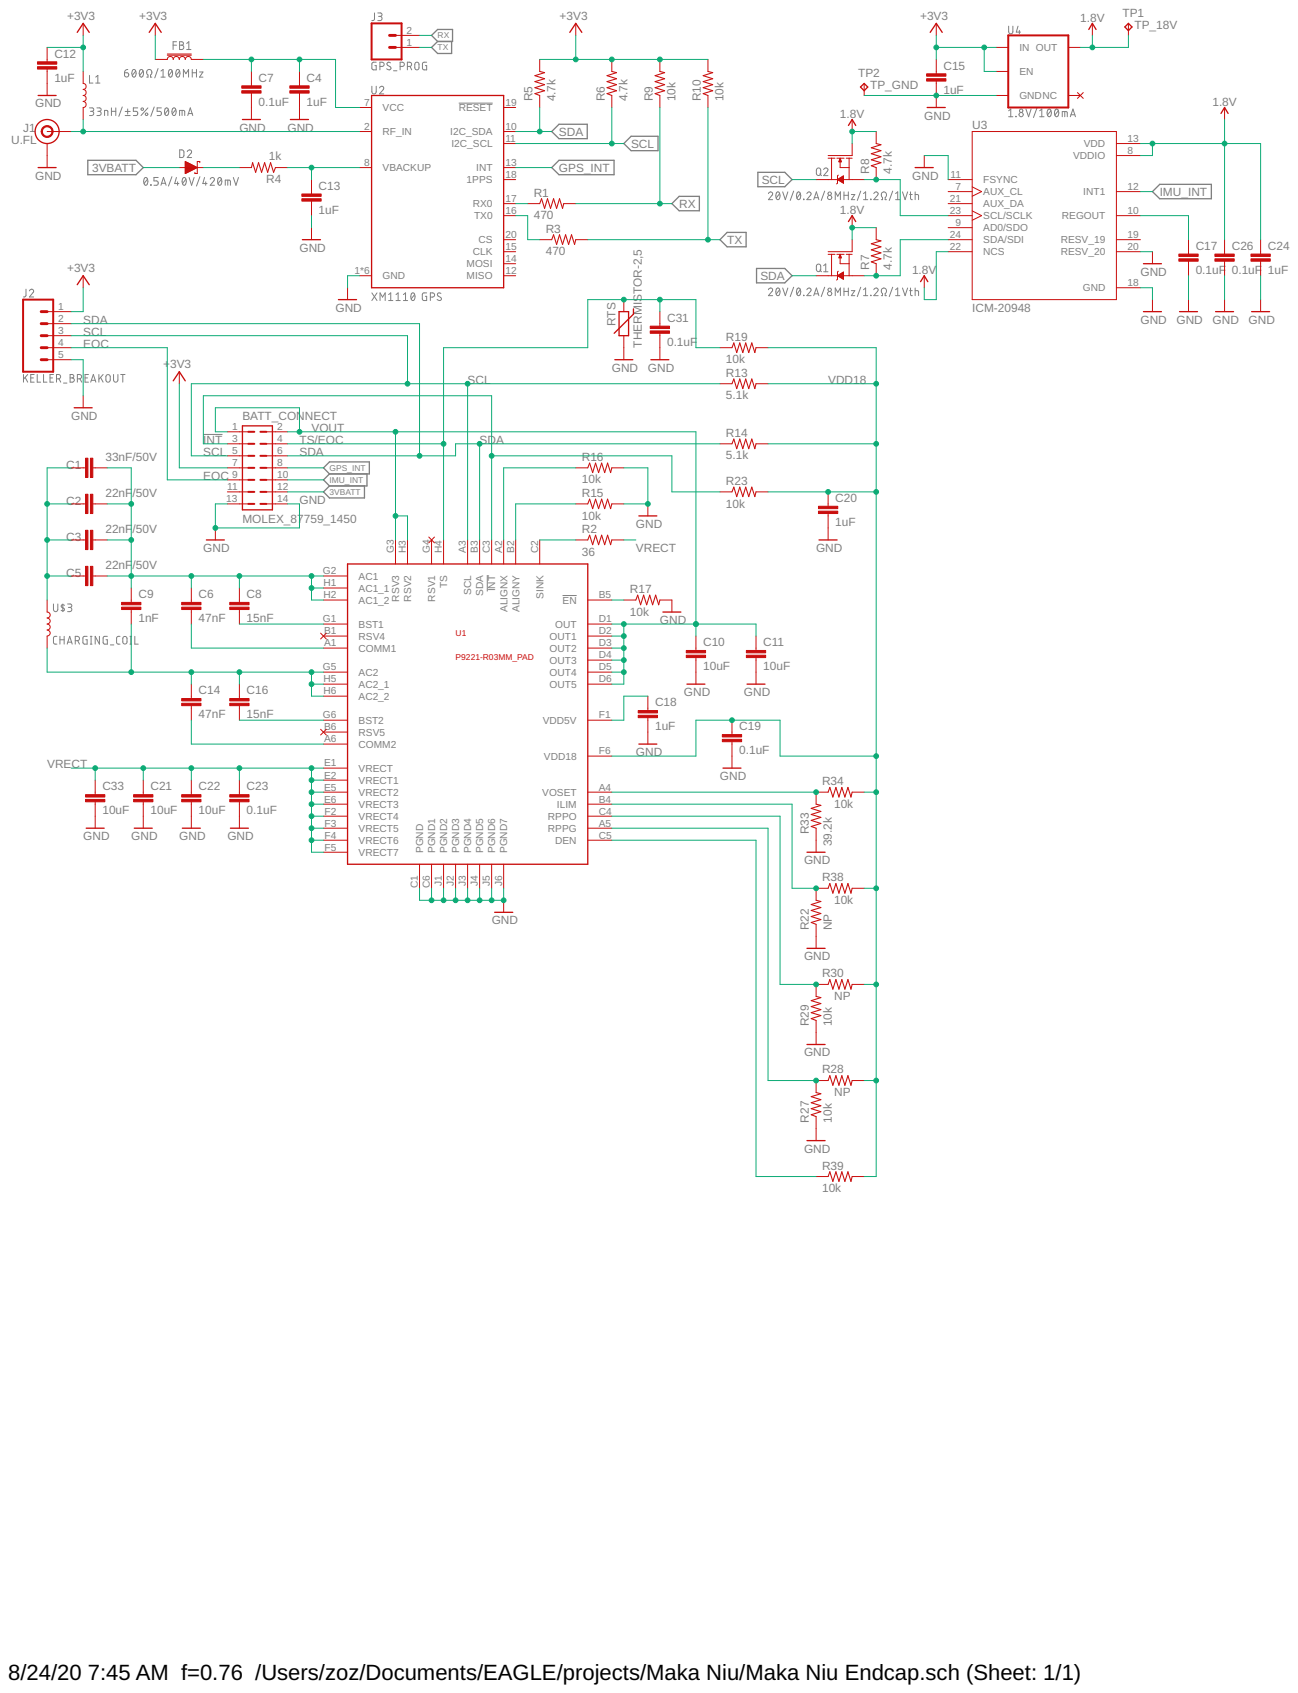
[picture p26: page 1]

GND GND

8/24/20 7:45 AM f=0.76 /Users/zoz/Documents/EAGLE/projects/Maka Niu/Maka Niu Endcap.sch (Sheet: 1/1)

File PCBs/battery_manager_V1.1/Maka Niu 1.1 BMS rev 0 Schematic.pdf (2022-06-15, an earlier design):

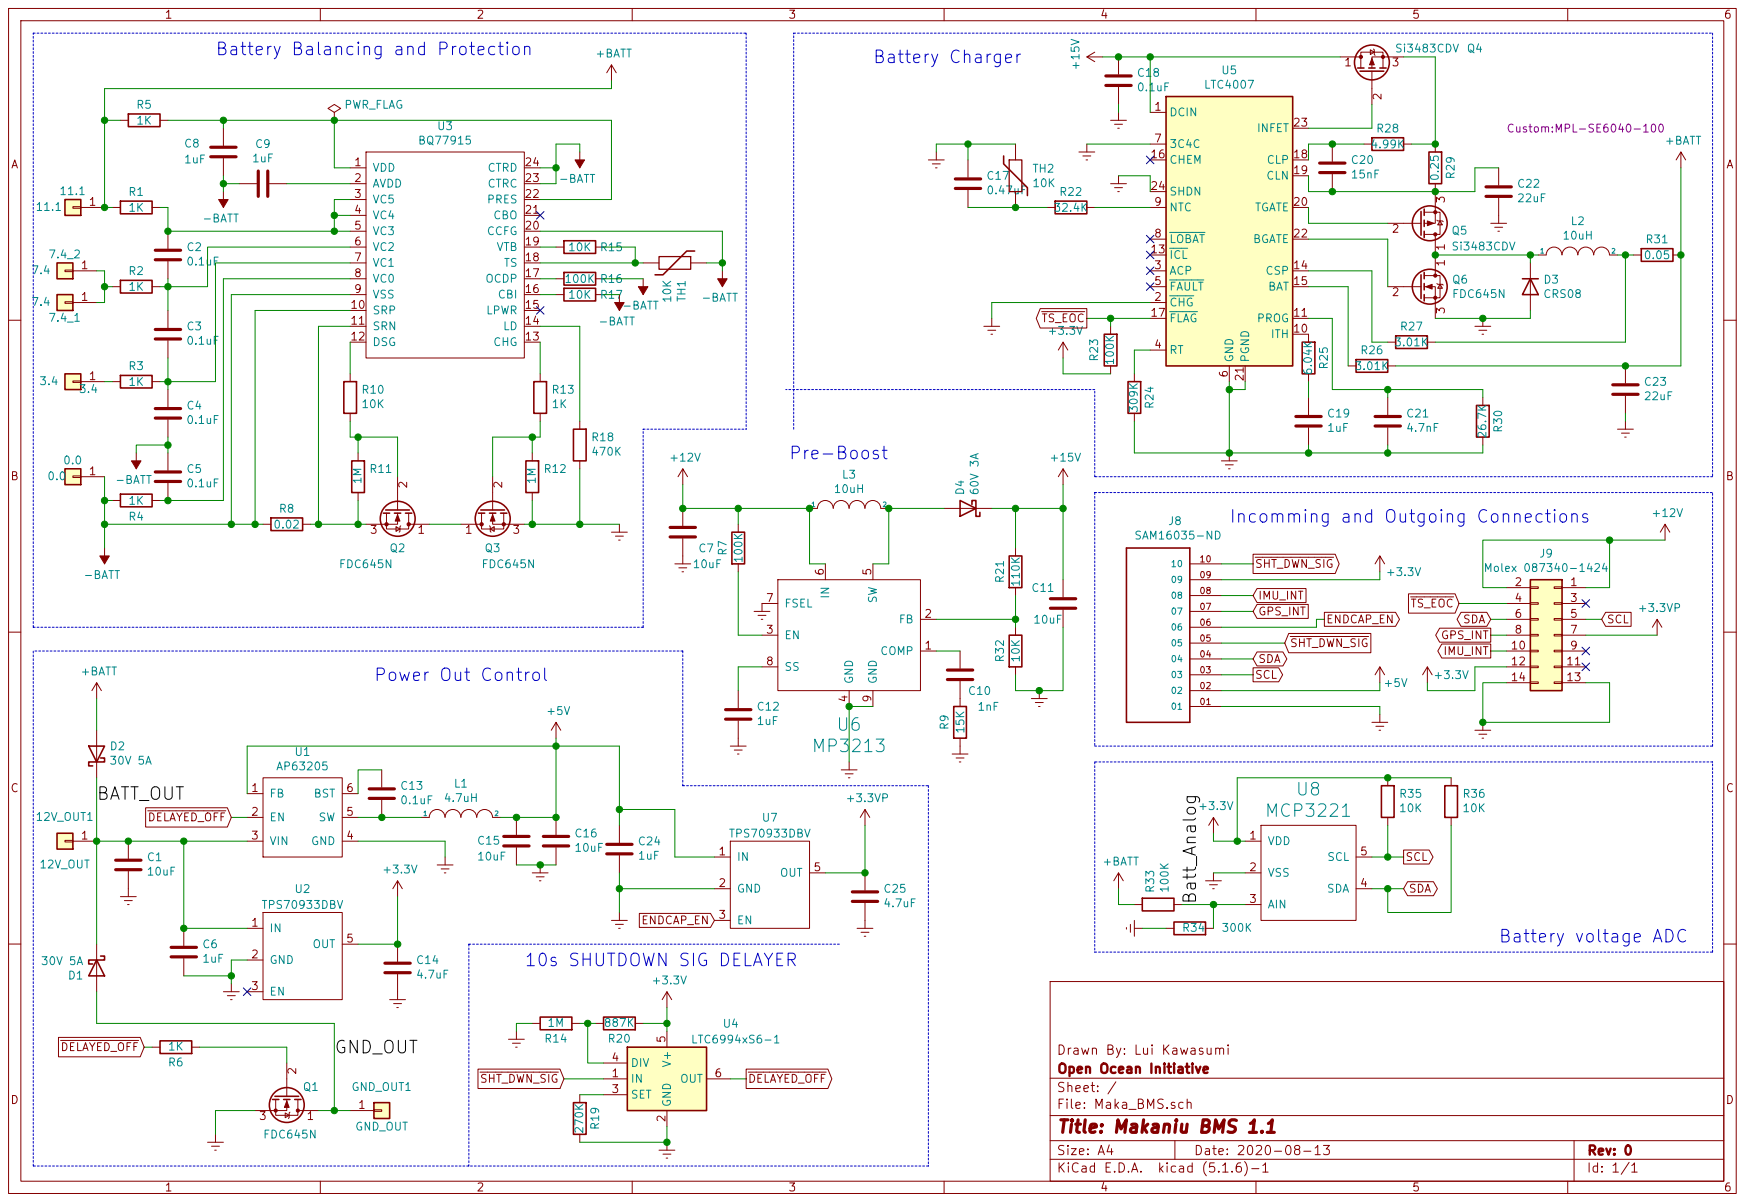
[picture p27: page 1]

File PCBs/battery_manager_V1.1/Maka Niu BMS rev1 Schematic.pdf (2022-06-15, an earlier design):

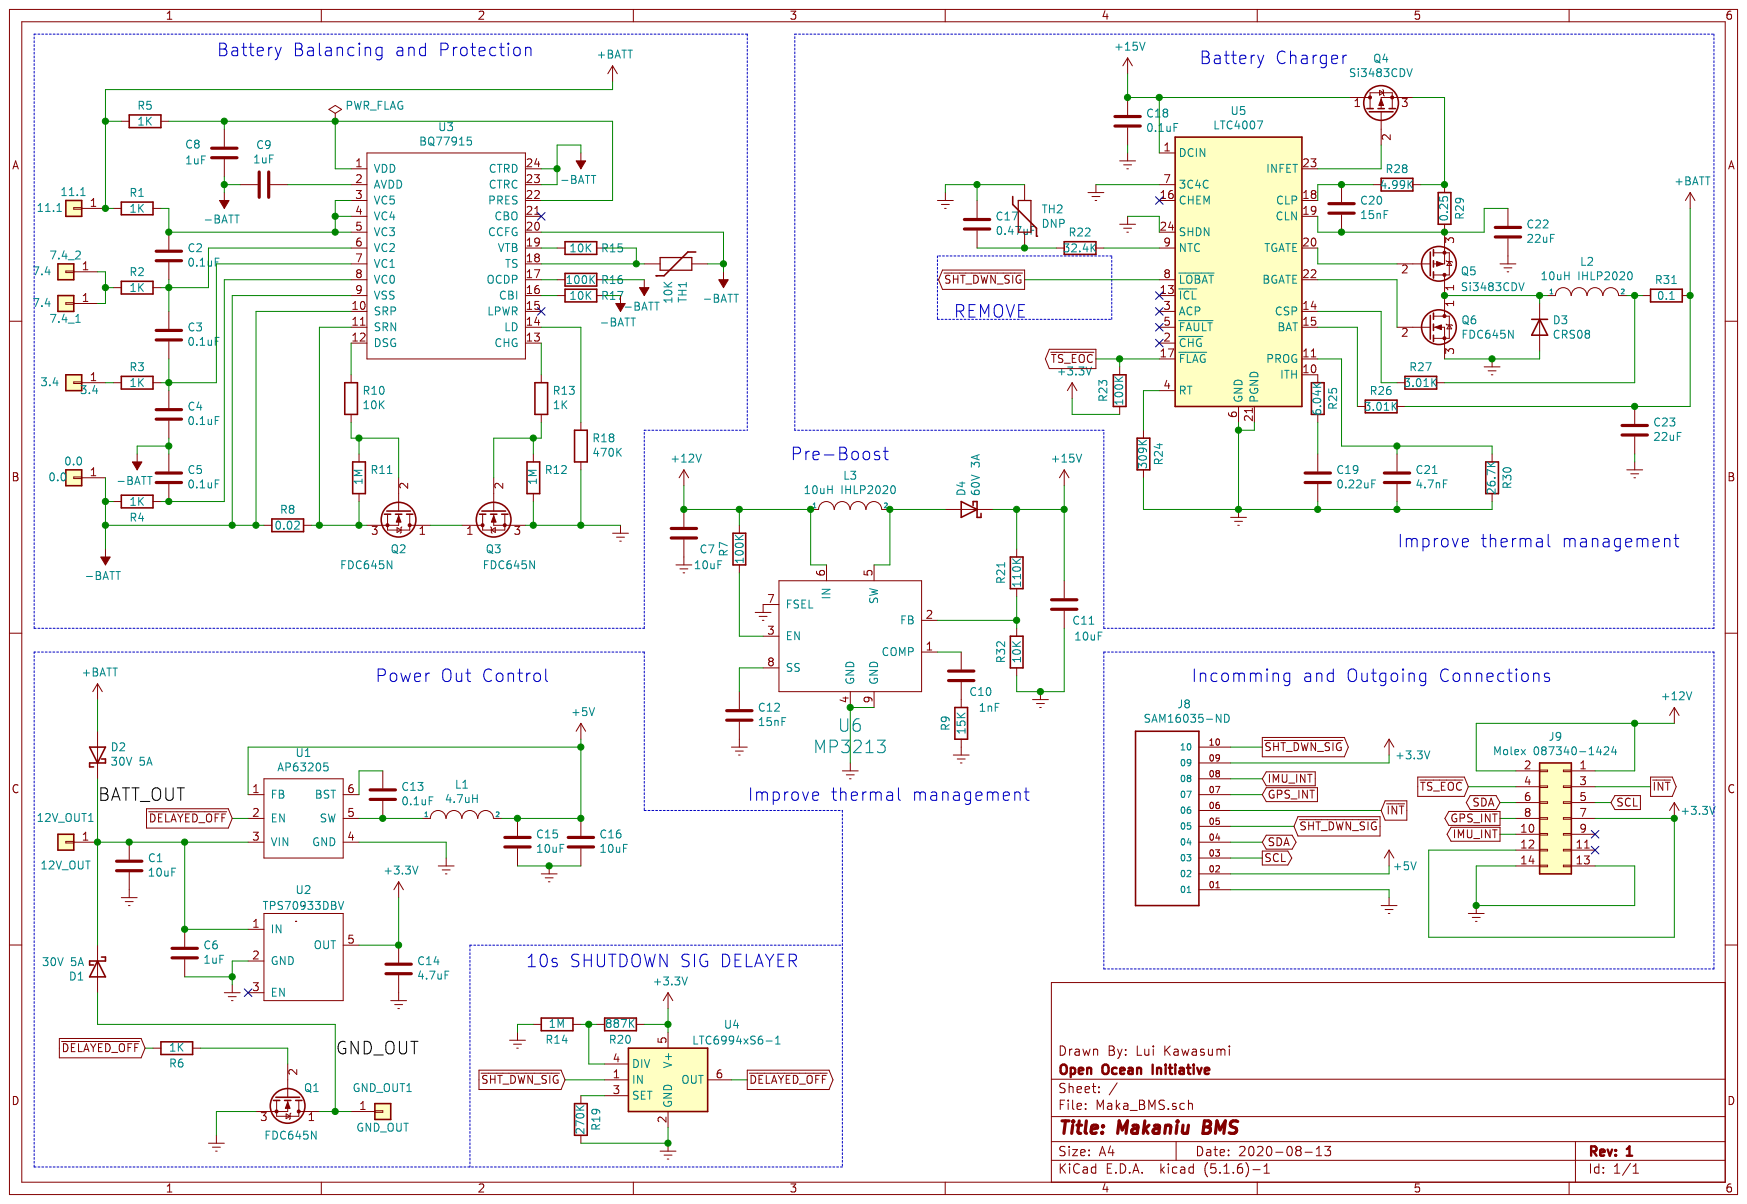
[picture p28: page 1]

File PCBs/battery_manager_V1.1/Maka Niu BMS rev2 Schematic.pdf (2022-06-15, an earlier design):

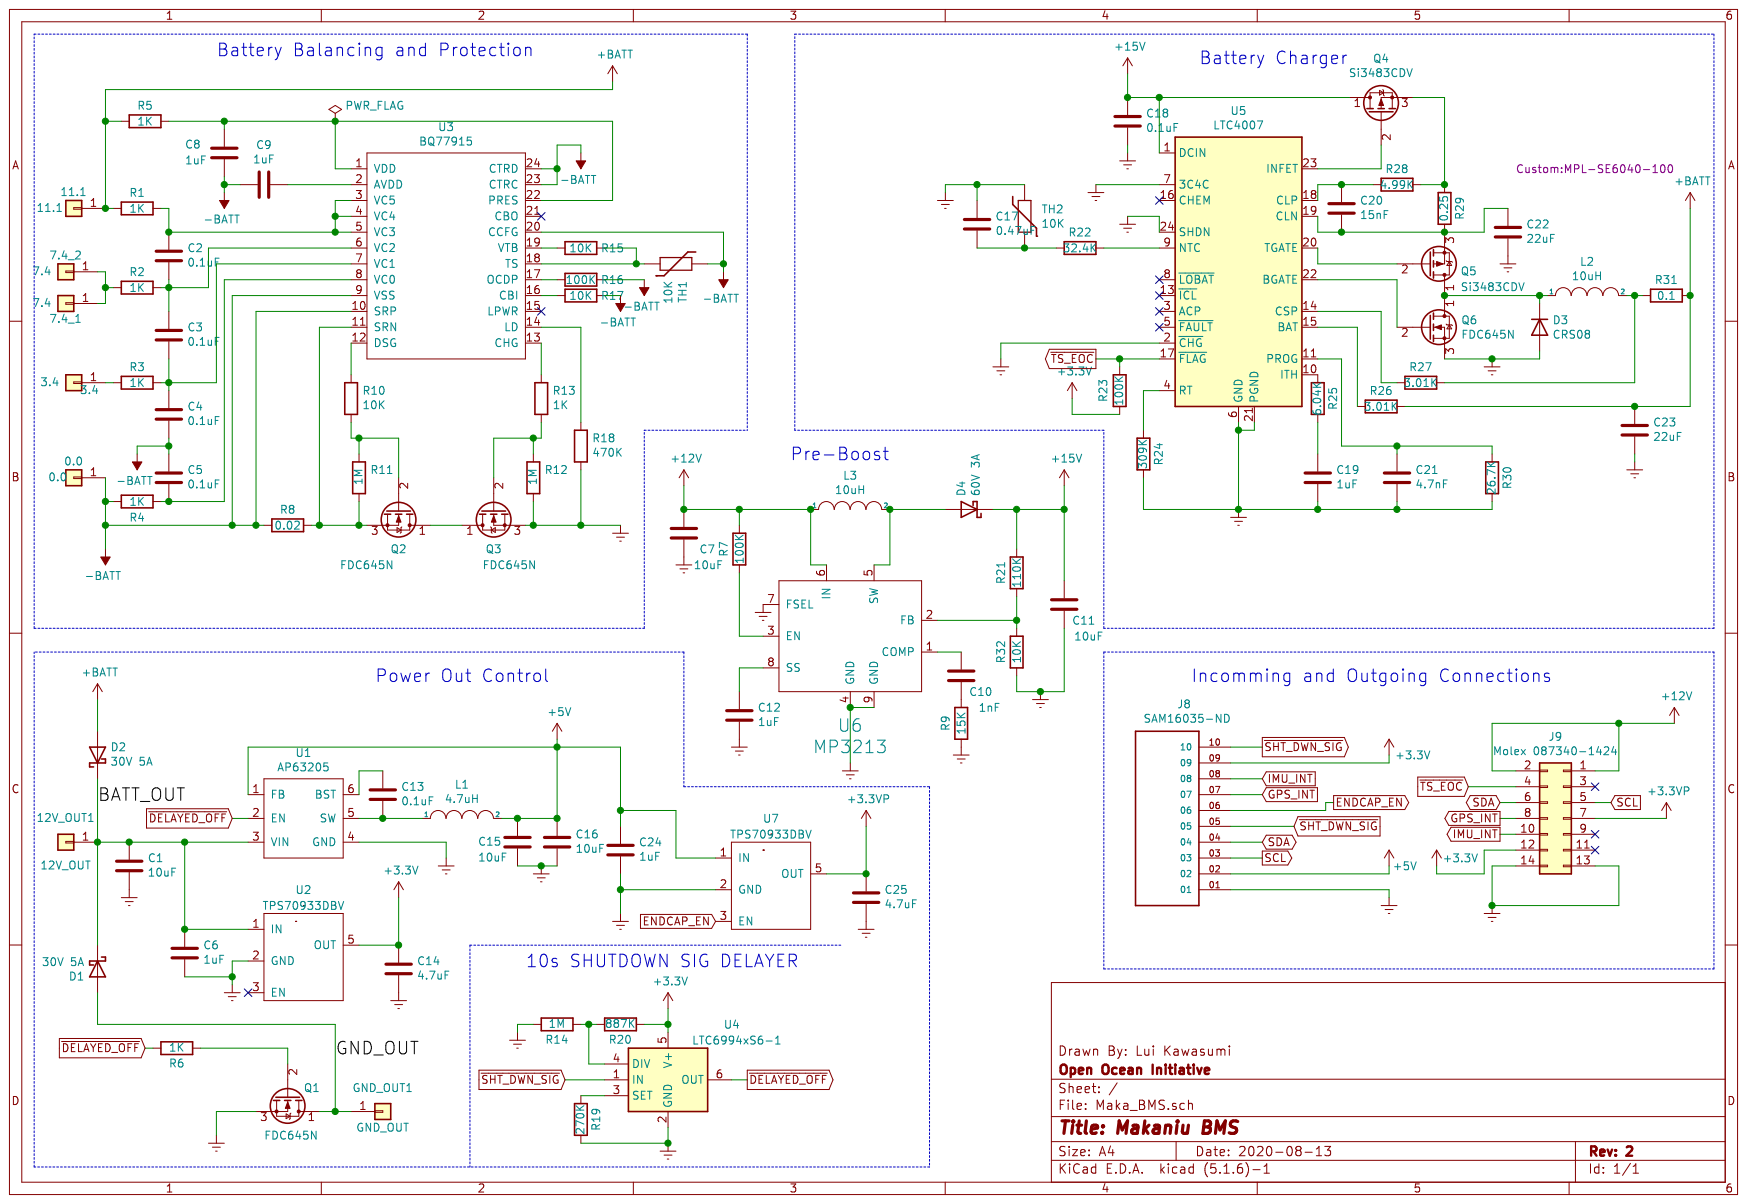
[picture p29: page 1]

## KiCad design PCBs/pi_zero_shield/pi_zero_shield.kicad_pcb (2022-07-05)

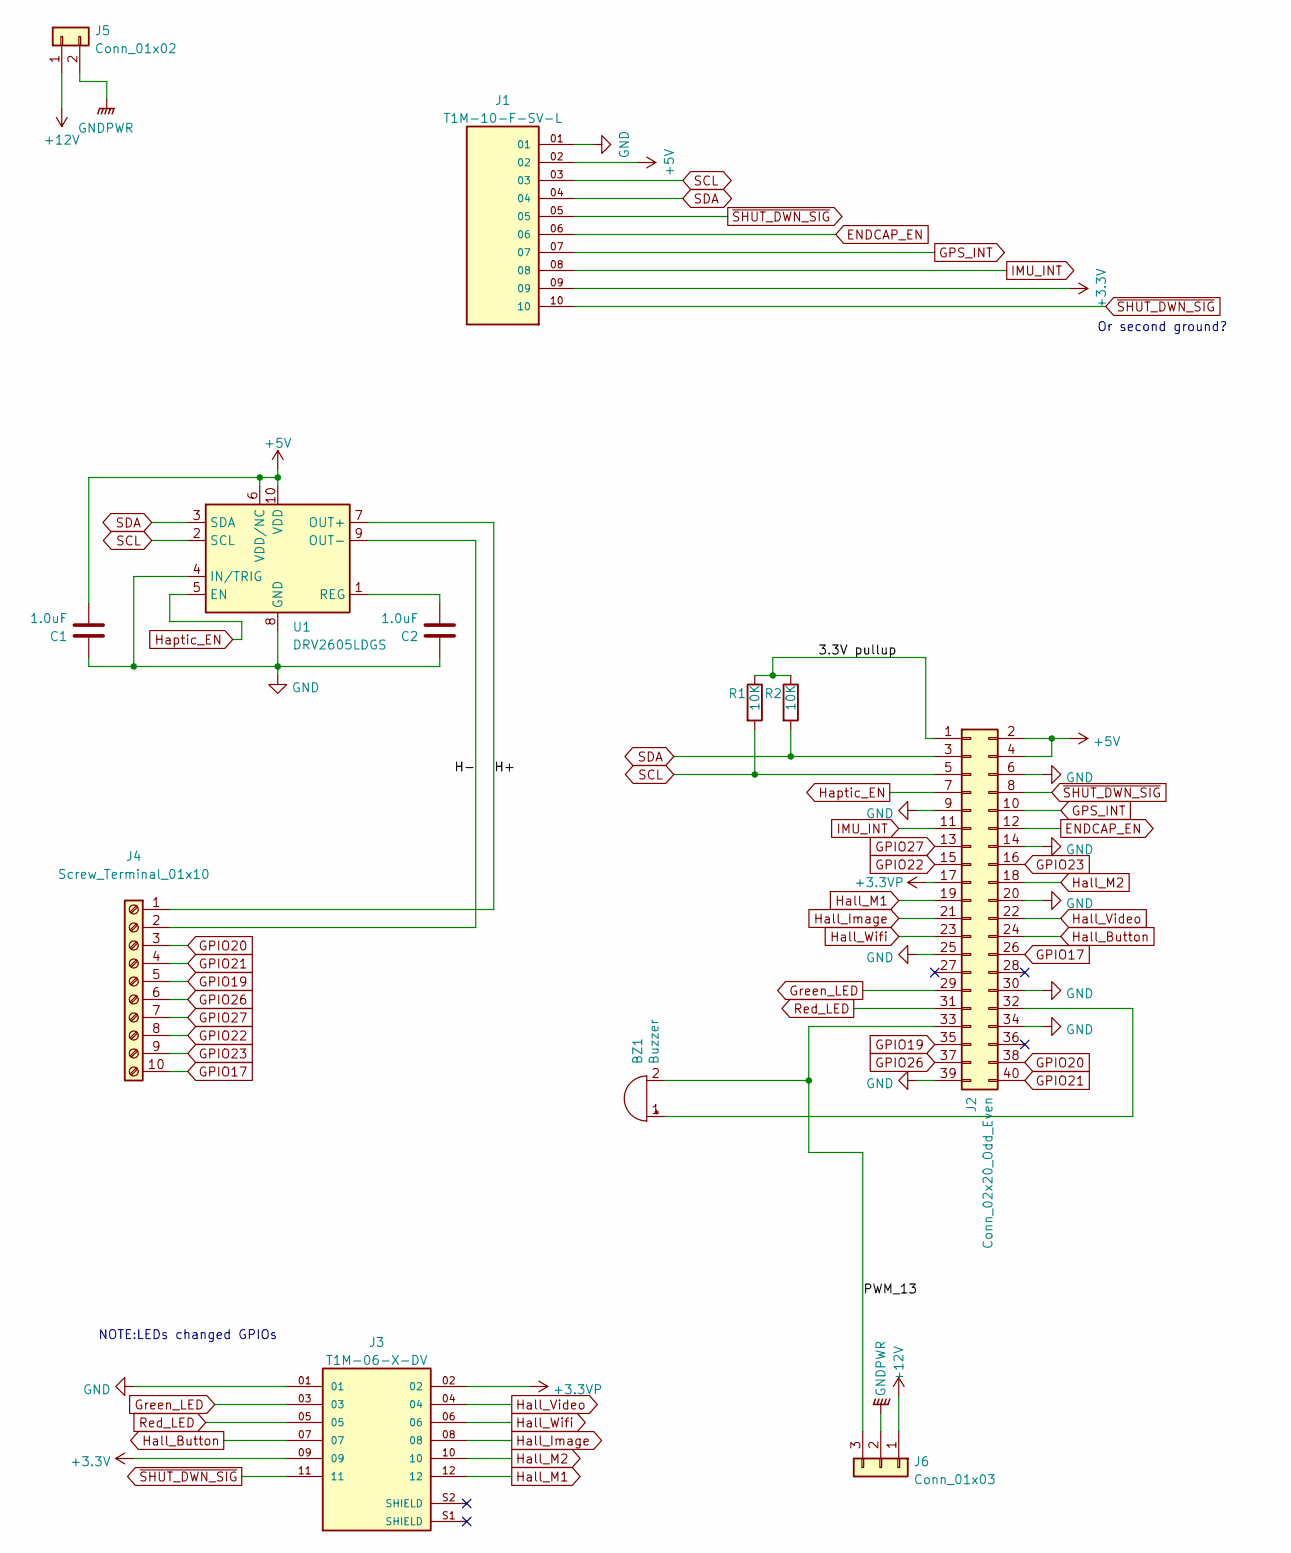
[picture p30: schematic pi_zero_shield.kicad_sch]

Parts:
BZ1: Buzzer; Buzzer_12x9.5RM7.6; LCSC C968749
C1, C2: 1.0uF; C_0603_1608Metric; LCSC C90540
J1: T1M-10-F-SV-L; SAMTEC_T1M-10-F-SV-L; Digikey SAM16035-ND
J2: Conn_02x20_Odd_Even; Pi_PinSocket_2x20; Digikey 952-3218-ND
J3: T1M-06-X-DV; SAMTEC_T1M-06-X-DV; Digikey -Get from Samtec
J4: Screw_Terminal_01x10; PinHeader_1x10_P2.54mm_Vertical; Digikey ED10567-ND
J5: Conn_01x02; Molex_Micro-Fit_3.0_43650-0210_1x02-1MP_P3.00mm_Horizontal; Digikey WM6264CT-ND
J6: Conn_01x03; Molex_Micro-Fit_3.0_43650-0310_1x03-1MP_P3.00mm_Horizontal; Digikey WM1886CT-ND
R1, R2: 10K; R_0603_1608Metric; LCSC C25804
U1: DRV2605LDGS; VSSOP-10_3x3mm_P0.5mm; LCSC C527464

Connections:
+3.3VP: J2.17, J3.02
+3V3: J1.09, J3.09
+5V: C1.1, J1.02, J2.2, J2.4, U1.6 (VDD/NC), U1.10 (VDD)
+12V: J5.1, J6.1
/3.3V pullup: J2.1, R1.1, R2.1
/H+: J4.1, U1.7 (OUT+)
/H-: J4.2, U1.9 (OUT-)
/PWM_13: BZ1.2 (+), J2.33, J6.3
ENDCAP_EN: J1.06, J2.12
GND: C1.2, C2.2, J1.01, J2.6, J2.9, J2.14, J2.20, J2.25, J2.30, J2.34, J2.39, J3.01, U1.4 (IN/TRIG), U1.8 (GND)
GNDPWR: J5.2, J6.2
GPIO17: J2.26, J4.10
GPIO19: J2.35, J4.5
GPIO20: J2.38, J4.3
GPIO21: J2.40, J4.4
GPIO22: J2.15, J4.8
GPIO23: J2.16, J4.9
GPIO26: J2.37, J4.6
GPIO27: J2.13, J4.7
GPS_INT: J1.07, J2.10
Green_LED: J2.29, J3.03
Hall_Button: J2.24, J3.07
Hall_Image: J2.21, J3.08
Hall_M1: J2.19, J3.12
Hall_M2: J2.18, J3.10
Hall_Video: J2.22, J3.04
Hall_Wifi: J2.23, J3.06
Haptic_EN: J2.7, U1.5 (EN)
IMU_INT: J1.08, J2.11
unnamed: BZ1.1 (-), J2.32
unnamed: C2.1, U1.1 (REG)
Red_LED: J2.31, J3.05
SCL: J1.03, J2.5, R1.2, U1.2 (SCL)
SDA: J1.04, J2.3, R2.2, U1.3 (SDA)
~SHUT_DWN_SIG: J1.05, J1.10, J2.8, J3.11

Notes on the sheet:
NOTE:LEDs changed GPIOs
Or second ground?

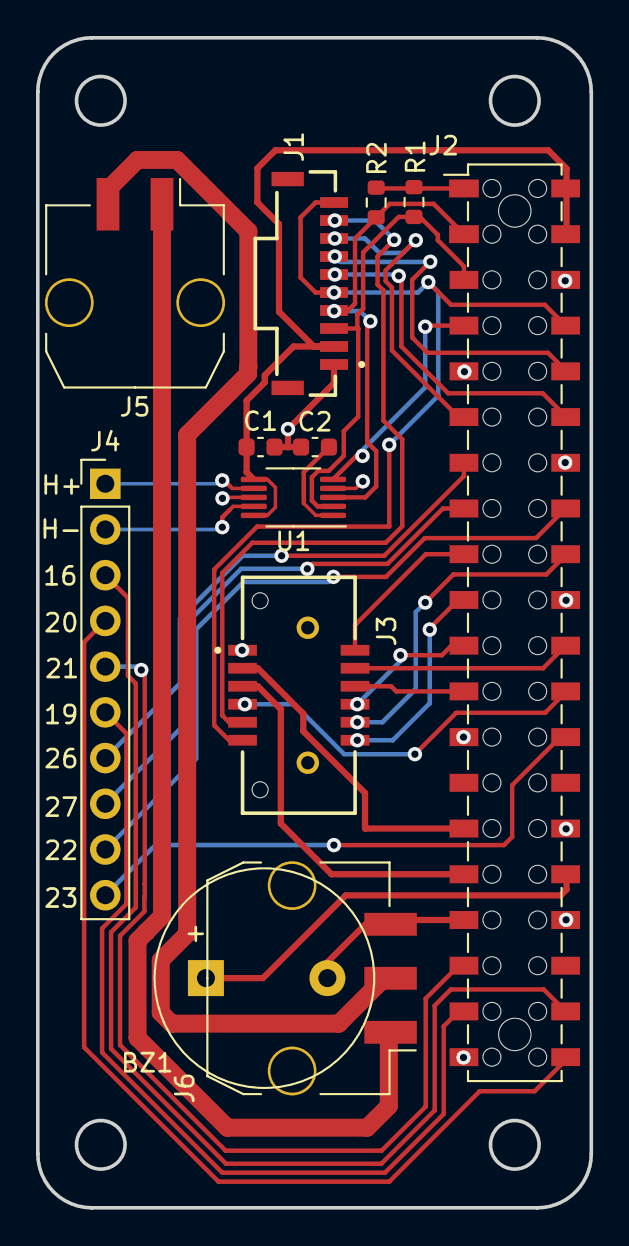
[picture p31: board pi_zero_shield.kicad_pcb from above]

Board: 2 copper layers, 30.8 x 65.0 mm, 12 parts (0 on the bottom side), 35 nets.

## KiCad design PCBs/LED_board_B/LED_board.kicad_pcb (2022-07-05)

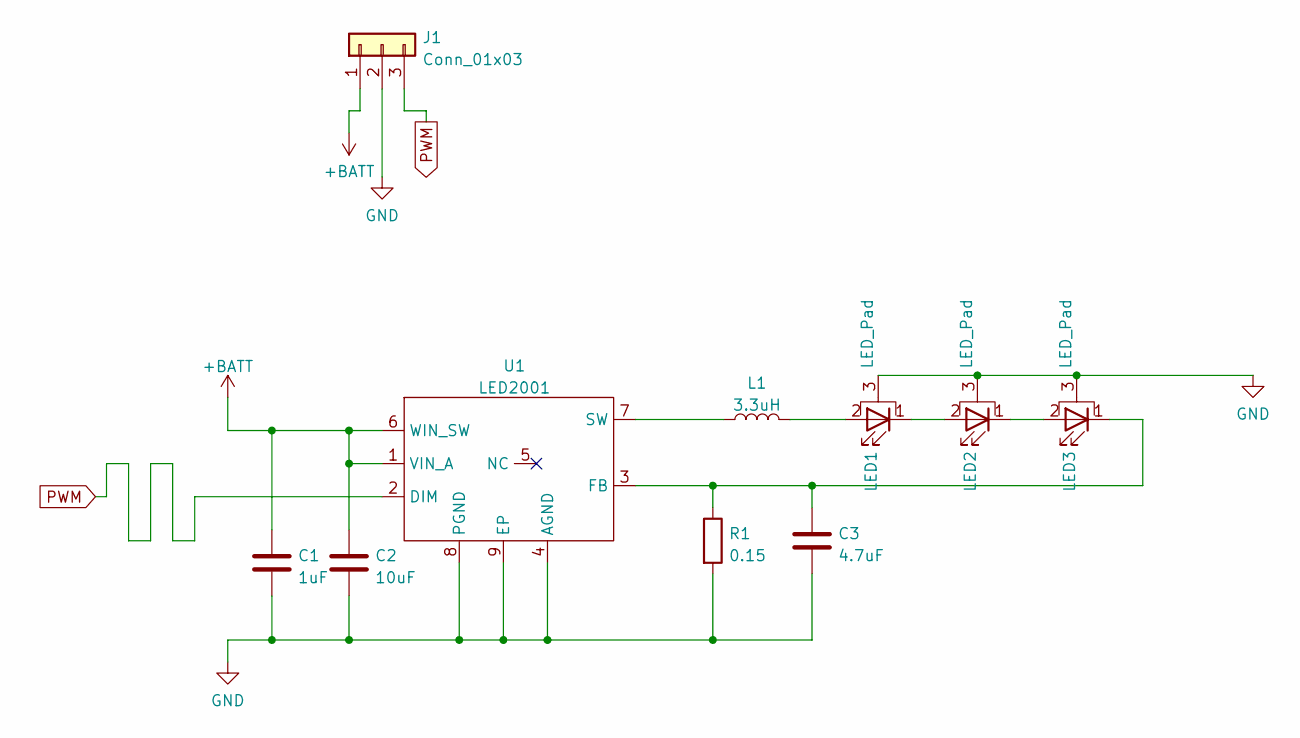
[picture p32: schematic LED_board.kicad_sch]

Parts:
C1: 1uF; C_0805_2012Metric; LCSC C28323
C2: 10uF; C_1210_3225Metric; LCSC C170073
C3: 4.7uF; C_1210_3225Metric; LCSC C384711
J1: Conn_01x03; Molex_Micro-Fit_3.0_43650-0324_1x03-1MP_P3.00mm_Vertical; Digikey WM3887CT-ND
L1: 3.3uH; ASWPA8050S; LCSC C340237
LED1, LED2, LED3: LED_Pad; LED_Cree-XHP50_6V; Digikey XMLBWT-00-0000-0000U2050CT-ND
R1: 0.15; R_2512_6332Metric; LCSC C176046
U1: LED2001; HSOP-8-1EP_3.9x4.9mm_P1.27mm_EP2.41x3.1mm; LCSC C2678918

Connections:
+BATT: C1.1, C2.1, J1.1, U1.1 (VIN_A), U1.6 (WIN_SW)
GND: C1.2, C2.2, C3.2, J1.2, LED1.3 (PAD), LED2.3 (PAD), LED3.3 (PAD), R1.2, U1.4 (AGND), U1.8 (PGND), U1.9 (EP)
unnamed: C3.1, LED3.1 (K), R1.1, U1.3 (FB)
unnamed: L1.1, U1.7 (SW)
unnamed: L1.2, LED1.2 (A)
unnamed: LED1.1 (K), LED2.2 (A)
unnamed: LED2.1 (K), LED3.2 (A)
PWM: J1.3, U1.2 (DIM)

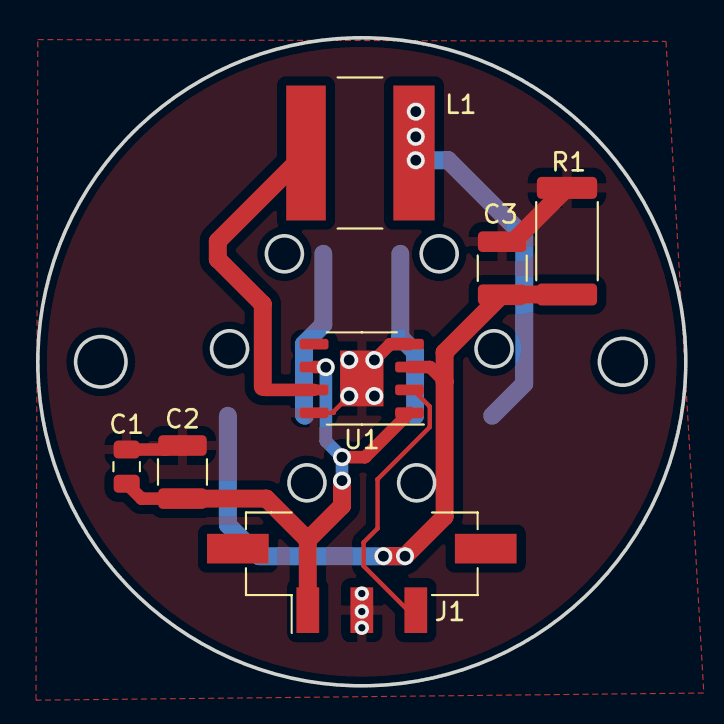
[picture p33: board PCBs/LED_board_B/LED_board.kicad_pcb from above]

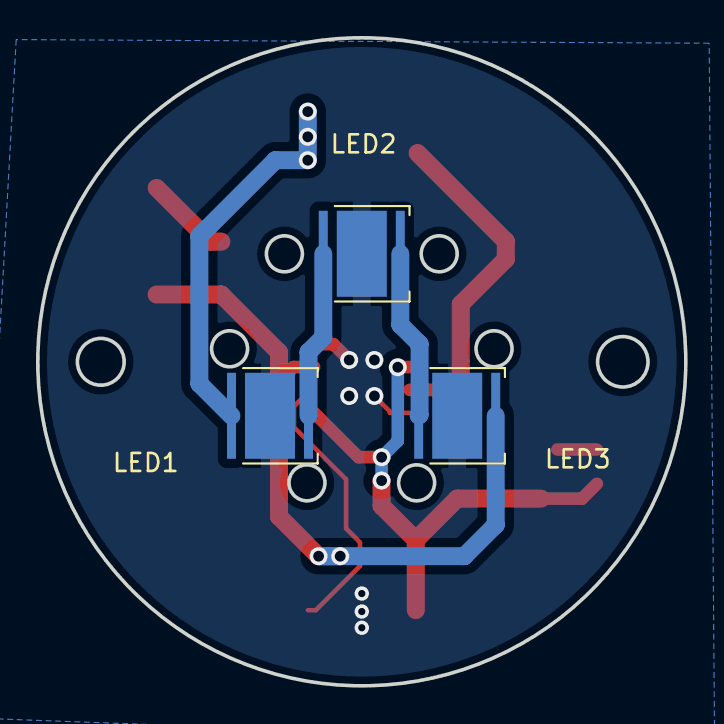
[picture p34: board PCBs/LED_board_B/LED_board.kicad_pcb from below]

Board: 2 copper layers, 36.0 x 36.0 mm, 10 parts (3 on the bottom side), 8 nets.

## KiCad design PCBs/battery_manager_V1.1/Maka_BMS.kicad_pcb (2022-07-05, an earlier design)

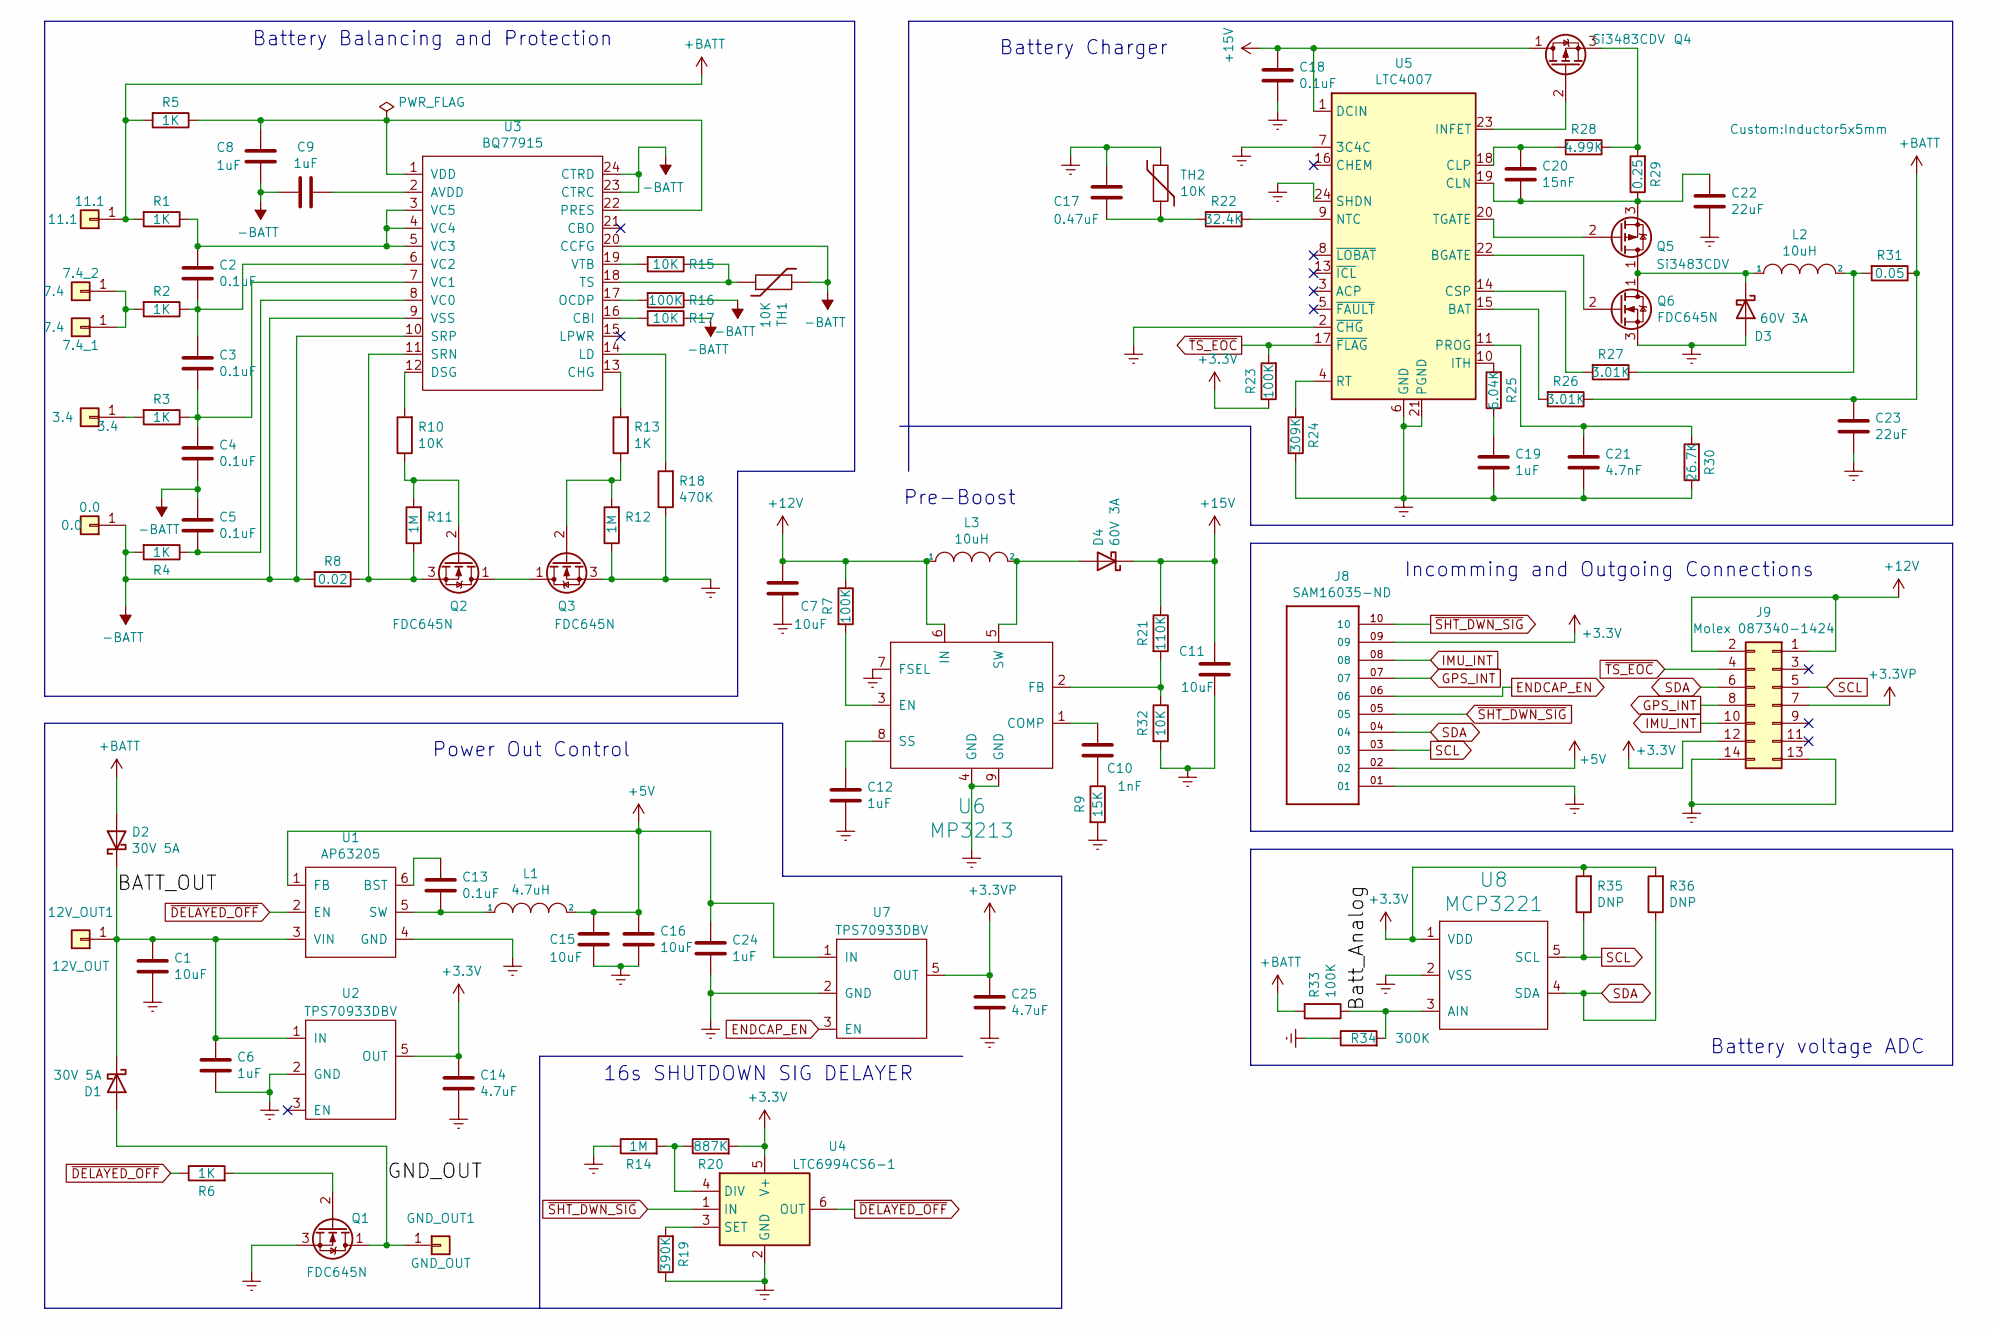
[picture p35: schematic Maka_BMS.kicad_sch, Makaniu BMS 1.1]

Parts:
0.0: 0.0; TruHole_Batter_Contact_Pad_with_9mm_clear; Digikey 36-240-ND
3.4: 3.4; TestPoint_THTPad_D1.5mm_Drill0.7mm
7.4_1, 7.4_2: 7.4; TruHole_Batter_Contact_Pad_with_9mm_clear; Digikey 36-240-ND
11.1: 11.1; TestPoint_THTPad_D1.5mm_Drill0.7mm
12V_OUT1: 12V_OUT; TestPoint_THTPad_D1.5mm_Drill0.7mm
C1, C7, C11, C15, C16: 10uF; C_0603_1608Metric; Digikey 490-7202-1-ND
C2, C3, C4, C5, C13, C18: 0.1uF; C_0402_1005Metric; Digikey 732-7495-1-ND
C6, C8, C9, C12, C19, C24: 1uF; C_0402_1005Metric; Digikey 490-10017-1-ND
C10: 1nF; C_0402_1005Metric; Digikey 478-1101-2-ND
C14, C25: 4.7uF; C_0603_1608Metric; Digikey 1276-1900-1-ND
C17: 0.47uF; C_0402_1005Metric; Digikey 490-12269-1-ND
C20: 15nF; C_0402_1005Metric; Digikey 311-1713-1-ND
C21: 4.7nF; C_0402_1005Metric; Digikey 311-1039-1-ND
C22, C23: 22uF; C_0603_1608Metric; Digikey 1276-7076-1-ND
D1, D2: 30V 5A; D_SMA; Digikey SK56A-LTPMSTR-ND
D3, D4: 60V 3A; D_SOD-123EP; Digikey SSA36CT-ND
GND_OUT1: GND_OUT; TestPoint_THTPad_D1.5mm_Drill0.7mm
J8: ‎SAM16035-ND‎; SAMTEC_T1M-10-F-SH-L-K; Digikey SAM11993-ND
J9: Molex 087340-1424; Molex_87340-1424_B; Digikey 23-0873401424-ND
L1: 4.7uH; L_1008_2520Metric; Digikey 490-10651-1-ND
L2, L3: 10uH; Inductor5x5mm; Digikey 1589-MPL-SE6040-100CT-ND
Q1, Q2, Q3, Q6: FDC645N; SOT-23-6_mosfet; Digikey FDC655BNCT-ND
Q4, Q5: Si3483CDV; SOT-23-6_mosfet; Digikey CPH6350-TL-WOSCT-ND
R1, R2, R3, R4, R5, R6, R13: 1K; R_0402_1005Metric; Digikey YAG1234CT-ND
R7, R16, R23, R33: 100K; R_0402_1005Metric; Digikey 311-100KLRCT-ND
R8: 0.02; R_1206_3216Metric; Digikey WSLP-.02CT-ND
R9: 15K; R_0402_1005Metric; Digikey 311-15.0KLRTR-ND
R10, R15, R17, R32: 10K; R_0402_1005Metric; Digikey 311-10.0KLRCT-ND
R11, R12, R14: 1M; R_0402_1005Metric; Digikey 311-1.00MLRCT-ND
R18: 470K; R_0402_1005Metric; Digikey 311-470KJRCT-ND
R19: 390K; R_0402_1005Metric; Digikey YAG3143CT-ND
R20: 887K; R_0402_1005Metric; Digikey YAG5696CT-ND
R21: 110K; R_0402_1005Metric; Digikey 311-110KLRCT-ND
R22: 32.4K; R_0402_1005Metric; Digikey YAG3119CT-ND
R24: 309K; R_0402_1005Metric; Digikey YAG3108CT-ND
R25: 6.04K; R_0402_1005Metric; Digikey YAG2293CT-ND
R26, R27: 3.01K; R_0402_1005Metric; Digikey 311-3.01KLRCT-ND
R28: 4.99K; R_0402_1005Metric; Digikey YAG1447CT-ND
R29: 0.25; R_1206_3216Metric; Digikey 311-0.25ANCT-ND
R30: 26.7K; R_0402_1005Metric; Digikey YAG3081CT-ND
R31: 0.05; R_1206_3216Metric; Digikey MCS1632R050FERCT-ND
R34: 300K; R_0402_1005Metric; Digikey 311-300KLRCT-ND
R35, R36: DNP; R_0402_1005Metric
TH1: 10K; R_0402_1005Metric; Digikey 495-5814-1-ND
TH2: 10K; R_0402_1005Metric; Digikey 311-10.0KLRCT-ND
U1: AP63205; TSOT-23-6; Digikey AP63205WU-7DICT-ND
U2, U7: TPS70933DBV; SOT-23-5; Digikey 497-6979-1-ND
U3: BQ77915; TSSOP-24_4.4x7.8mm_P0.65mm; Digikey 296-50995-1-ND
U4: LTC6994CS6-1; TSOT-23-6; Digikey LTC6994CS6-1#TRMPBFCT-ND
U5: LTC4007; SSOP-24_3.9x8.7mm_P0.635mm; Digikey LTC4007EGN#PBF-ND
U6: MP3213; MSOP-8-1EP_3x3mm_P0.65mm_EP1.95x2.15mm; Digikey 1589-1626-1-ND
U8: MCP3221; SOT-23-5; LCSC C36310

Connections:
+3.3VP: C25.2, J9.7, U7.5 (OUT)
+3V3: C14.2, J8.09, J9.12, R20.2, R23.1, R35.2, R36.2, U2.5 (OUT), U4.5 (V+), U8.1 (VDD)
+5V: C15.2, C16.2, C24.2, J8.02, L1.2, U1.1 (FB), U7.1 (IN)
+12V: C7.1, J9.1, J9.2, L3.1, R7.1, U6.6 (IN)
+15V: C11.1, C18.2, D4.1 (K), Q4.1 (D), R21.1, U5.1 (DCIN)
+BATT: 11.1.1, C23.2, D2.2 (A), R1.2, R5.2, R26.1, R31.1, R33.2
-BATT: 0.0.1, C4.1, C5.2, C8.1, C9.2, R4.2, R8.2, R16.1, R17.1, TH1.1, U3.9 (VSS), U3.10 (SRP), U3.20 (CCFG), U3.23 (CTRC), U3.24 (CTRD)
/BATT_OUT: 12V_OUT1.1, C1.2, C6.2, D1.1 (K), D2.1 (K), U1.3 (VIN), U2.1 (IN)
/Batt_Analog: R33.1, R34.2, U8.3 (AIN)
/GND_OUT: D1.2 (A), GND_OUT1.1, Q1.1 (D)
ENDCAP_EN: J8.06, U7.3 (EN)
Earth: C1.1, C6.1, C7.2, C11.2, C12.1, C14.1, C15.1, C16.1, C17.2, C18.1, C19.1, C21.1, C22.1, C23.1, C24.1, C25.1, D3.2 (A), J8.01, J9.13, J9.14, Q1.3 (S), Q3.3 (S), Q6.3 (S), R9.2, R12.1, R14.1, R18.1, R19.1, R24.1, R30.1, R32.2, R34.1, TH2.1, U1.4 (GND), U2.2 (GND), U4.2 (GND), U5.2 (~CHG), U5.6 (GND), U5.7 (3C4C), U5.21 (PGND), U5.24 (SHDN), U6.4 (GND), U6.7 (FSEL), U6.9 (GND), U7.2 (GND), U8.2 (VSS)
GPS_INT: J8.07, J9.8
IMU_INT: J8.08, J9.10
unnamed: 3.4.1, R3.2
unnamed: 7.4_1.1, 7.4_2.1, R2.2
unnamed: C2.1, C3.2, R2.1, U3.6 (VC2)
unnamed: C2.2, R1.1, U3.3 (VC5), U3.4 (VC4), U3.5 (VC3)
unnamed: C3.1, C4.2, R3.1, U3.7 (VC1)
unnamed: C5.1, R4.1, U3.8 (VC0)
unnamed: C8.2, R5.1, U3.1 (VDD), U3.22 (PRES)
unnamed: C9.1, U3.2 (AVDD)
unnamed: C10.1, U6.1 (COMP)
unnamed: C10.2, R9.1
unnamed: C12.2, U6.8 (SS)
unnamed: C13.1, L1.1, U1.5 (SW)
unnamed: C13.2, U1.6 (BST)
unnamed: C17.1, R22.2, TH2.2
unnamed: C19.2, R25.1
unnamed: C20.1, C22.2, Q5.3 (S), R29.1, U5.19 (CLN)
unnamed: C20.2, R28.2, U5.18 (CLP)
unnamed: C21.2, R30.2, U5.11 (PROG)
unnamed: D4.2 (A), L3.2, U6.5 (SW)
unnamed: D3.1 (K), L2.1, Q5.1 (D), Q6.1 (D)
unnamed: L2.2, R27.1, R31.2
unnamed: Q1.2 (G), R6.2
unnamed: Q2.1 (D), Q3.1 (D)
unnamed: Q2.2 (G), R10.1, R11.2
unnamed: Q2.3 (S), R8.1, R11.1, U3.11 (SRN)
unnamed: Q3.2 (G), R12.2, R13.1
unnamed: Q4.2 (G), U5.23 (INFET)
unnamed: Q4.3 (S), R28.1, R29.2
unnamed: Q5.2 (G), U5.20 (TGATE)
unnamed: Q6.2 (G), U5.22 (BGATE)
unnamed: R7.2, U6.3 (EN)
unnamed: R10.2, U3.12 (DSG)
unnamed: R13.2, U3.13 (CHG)
unnamed: R14.2, R20.1, U4.4 (DIV)
unnamed: R15.1, TH1.2, U3.18 (TS)
unnamed: R15.2, U3.19 (VTB)
unnamed: R16.2, U3.17 (OCDP)
unnamed: R17.2, U3.16 (CBI)
unnamed: R18.2, U3.14 (LD)
unnamed: R19.2, U4.3 (SET)
unnamed: R21.2, R32.1, U6.2 (FB)
unnamed: R22.1, U5.9 (NTC)
unnamed: R24.2, U5.4 (RT)
unnamed: R25.2, U5.10 (ITH)
unnamed: R27.2, U5.14 (CSP)
unnamed: R26.2, U5.15 (BAT)
SCL: J8.03, J9.5, R35.1, U8.5 (SCL)
SDA: J8.04, J9.6, R36.1, U8.4 (SDA)
~DELAYED_OFF: R6.1, U1.2 (EN), U4.6 (OUT)
~SHT_DWN_SIG: J8.05, J8.10, U4.1 (IN)
~TS_EOC: J9.4, R23.2, U5.17 (~FLAG)

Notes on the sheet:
Power Out Control
16s SHUTDOWN SIG DELAYER
Battery voltage ADC
Pre-Boost
Battery Charger
Battery Balancing and Protection
Incomming and Outgoing Connections

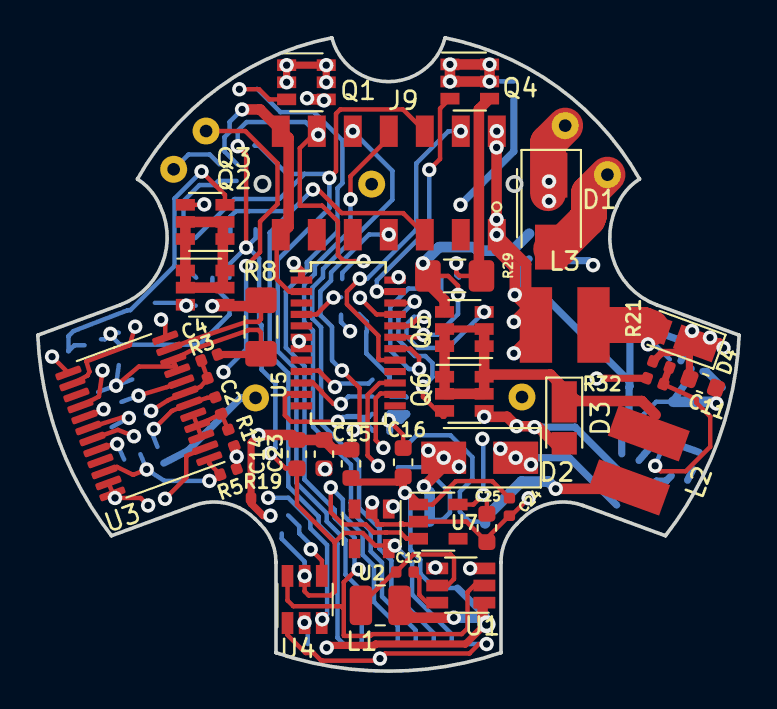
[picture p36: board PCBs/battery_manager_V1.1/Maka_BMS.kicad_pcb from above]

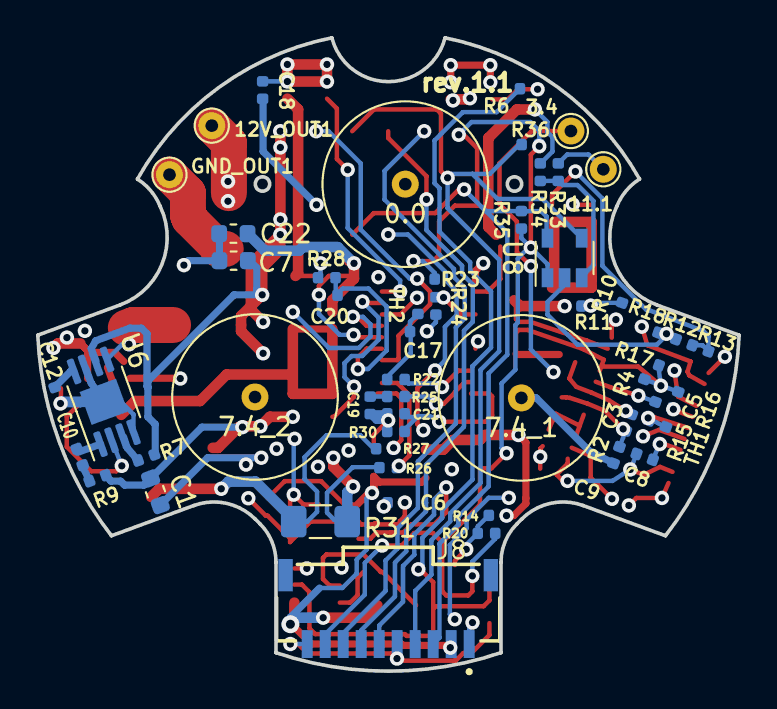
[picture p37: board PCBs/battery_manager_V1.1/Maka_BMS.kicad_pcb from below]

Board: 4 copper layers, 39.0 x 35.2 mm, 93 parts (55 on the bottom side), 65 nets.

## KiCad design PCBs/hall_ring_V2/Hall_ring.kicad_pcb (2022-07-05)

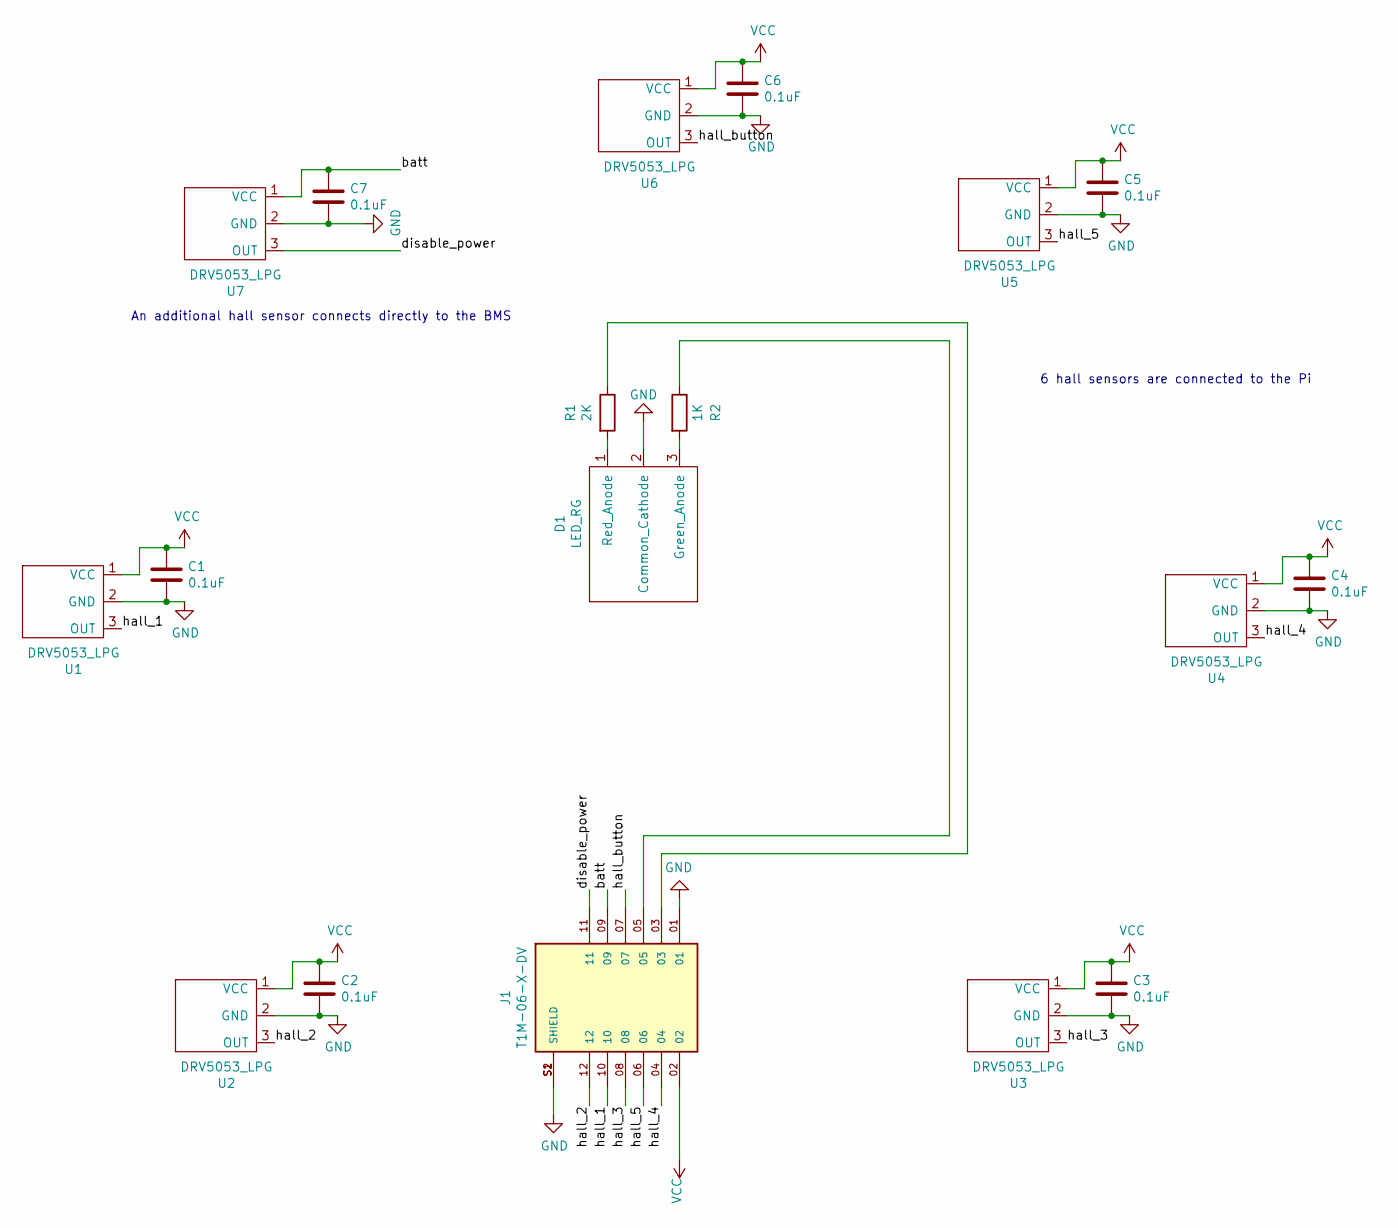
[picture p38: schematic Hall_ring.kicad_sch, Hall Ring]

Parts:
C1, C2, C3, C4, C5, C6, C7: 0.1uF; C_0402_1005Metric; Digikey 1276-1043-2-ND
D1: LED_RG; PinHeader_1x03_P2.00mm_Vertical; Digikey 160-1939-ND
J1: T1M-06-X-DV; SAMTEC_T1M-06-X-DV; Digikey ~ Get from Samtec
R1: 2K; R_0402_1005Metric; Digikey CR0402-FX-2001GLFCT-ND
R2: 1K; R_0402_1005Metric; Digikey RMCF0402FT1K00CT-ND
U1, U2, U3, U4, U5, U6, U7: DRV5053_LPG; TO-92Flat; Digikey 296-DRV5032DULPGMCT-ND

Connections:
/batt: C7.1, J1.09, U7.1 (VCC)
/disable_power: J1.11, U7.3 (OUT)
/hall_1: J1.10, U1.3 (OUT)
/hall_2: J1.12, U2.3 (OUT)
/hall_3: J1.08, U3.3 (OUT)
/hall_4: J1.04, U4.3 (OUT)
/hall_5: J1.06, U5.3 (OUT)
/hall_button: J1.07, U6.3 (OUT)
GND: C1.2, C2.2, C3.2, C4.2, C5.2, C6.2, C7.2, D1.2 (Common_Cathode), J1.01, J1.S1 (SHIELD), J1.S2 (SHIELD), U1.2 (GND), U2.2 (GND), U3.2 (GND), U4.2 (GND), U5.2 (GND), U6.2 (GND), U7.2 (GND)
unnamed: D1.1 (Red_Anode), R1.2
unnamed: D1.3 (Green_Anode), R2.2
unnamed: J1.03, R1.1
unnamed: J1.05, R2.1
VCC: C1.1, C2.1, C3.1, C4.1, C5.1, C6.1, J1.02, U1.1 (VCC), U2.1 (VCC), U3.1 (VCC), U4.1 (VCC), U5.1 (VCC), U6.1 (VCC)

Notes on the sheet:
6 hall sensors are connected to the Pi
An additional hall sensor connects directly to the BMS

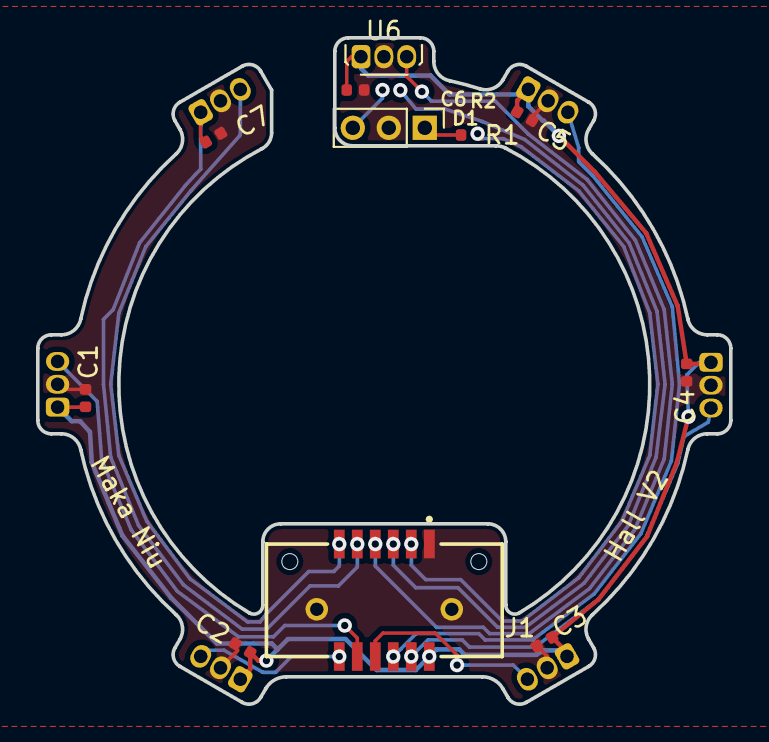
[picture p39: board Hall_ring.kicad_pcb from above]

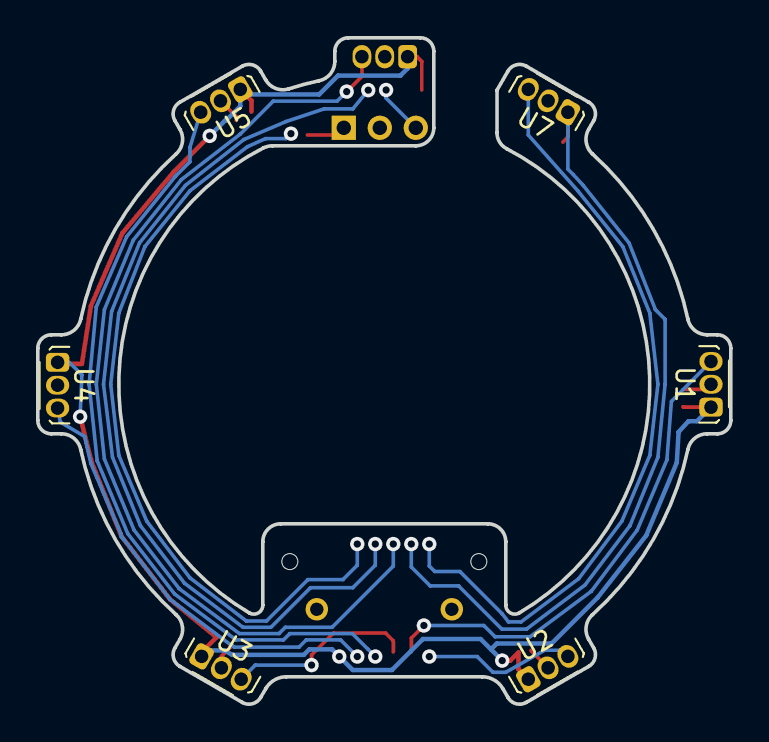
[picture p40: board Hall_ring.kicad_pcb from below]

Board: 2 copper layers, 38.5 x 37.0 mm, 18 parts (6 on the bottom side), 14 nets.

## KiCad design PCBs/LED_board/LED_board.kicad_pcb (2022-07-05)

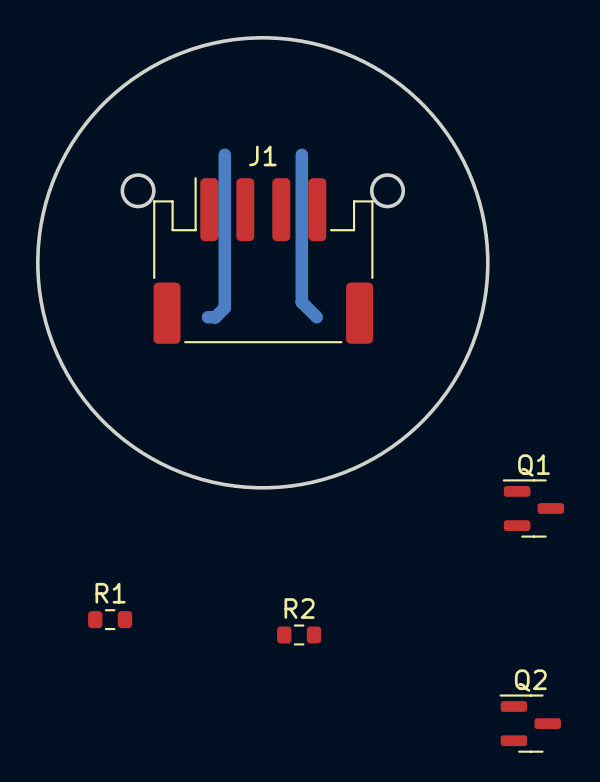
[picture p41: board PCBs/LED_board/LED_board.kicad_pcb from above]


Board: 2 copper layers, 25.0 x 25.0 mm, 8 parts (3 on the bottom side), 7 nets.

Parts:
D1, D2, D3: LED_Pad; LED_Cree-XHP50_6V
J1: S4B-PH-SM4; JST_PH_S4B-PH-SM4-TB_1x04-1MP_P2.00mm_Horizontal
Q1: Q_NPN_BCE; SOT-23
Q2: Q_NMOS_DGS; SOT-23
R1, R2: R; R_0603_1608Metric

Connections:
+BATT: D1.2 (A), J1.2, R1.1
GND: J1.1, Q1.3 (E), R2.2
unnamed: D1.1 (K), D2.2 (A)
unnamed: D2.1 (K), D3.2 (A)
unnamed: D3.1 (K), Q2.1 (D)
unnamed: Q1.1 (B), Q2.3 (S), R2.1
unnamed: Q1.2 (C), Q2.2 (G), R1.2

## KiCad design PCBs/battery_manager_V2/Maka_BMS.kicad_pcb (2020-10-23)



Board: 4 copper layers, 39.0 x 35.2 mm, 128 parts (79 on the bottom side), 89 nets, no tracks yet.

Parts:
0.0: 0; TruHole_Batter_Contact_Pad_with_9mm_clear
3.4: 3.4; TestPoint_THTPad_D1.5mm_Drill0.7mm
7.4_H1, 7.4_L1: 7.4; TruHole_Batter_Contact_Pad_with_9mm_clear
11.1: 11.1; TestPoint_THTPad_D1.5mm_Drill0.7mm
12V_OUT1: 12V_OUT; TestPoint_THTPad_D1.5mm_Drill0.7mm
C1, C15, C16, C123, C126: 10uF; C_0603_1608Metric
C2, C152, C153: 100pF; C_0402_1005Metric
C3, C4, C5, C10, C17, C119, C124, C156, C157: 0.1uF; C_0402_1005Metric
C6, C8, C9, C125, C137: 1uF; C_0402_1005Metric
C7: 4.7uF; C_0603_1608Metric
C11, C12: 0.033uF; C_0603_1608Metric
C13: 0.47uF; C_0805_2012Metric
C14, C138, C139: 0.047uF; C_0402_1005Metric
C114: 0.01uF; C_0402_1005Metric
C115, C160: 1000pF; C_0402_1005Metric
C116, C127, C128: 10uF; C_0805_2012Metric
C120, C136: 56uF; C_1206_3216Metric
C121, C122: 47uF; C_1206_3216Metric
C132, C135: 22uF; C_1206_3216Metric
C140: 33pF; C_0402_1005Metric
C142: 15pF; C_0402_1005Metric
C143: 1800pF; C_0402_1005Metric
C144: 680pF; C_0402_1005Metric
C151: 2.2uF; C_0402_1005Metric
C161, C165: 47pF; C_0402_1005Metric
D1, D2, D3: D_Schottky; D_SOD-123EP
D5: BAS5202VH6327; D_SC-79
GND_OUT1: GND_OUT; TestPoint_THTPad_D1.5mm_Drill0.7mm
J8: T1M-10-F-SH-L-K; SAMTEC_T1M-10-F-SH-L-K
J9: Molex 087340-1424; Molex_87340-1424_B
L1: 4.7uH; L_1008_2520Metric
L8: 2.2uH_Core_Iron; L_4.95x4.95_H2
NT2: Net-Tie_2; NetTie-2_SMD_Pad0.5mm
Q1, Q2, Q3: FDC645N; SOT-23-6_mosfet
Q4: BC817-16LT1G; SOT-23
Q5, Q6, Q7, Q8: CSD17308Q3; VSON-8_3.3x3.3mm_P0.65mm_NexFET
Q9: CSD25404Q3; VSON-8_3.3x3.3mm_P0.65mm_NexFET
Q10: DMG1012UW-7; SOT-23
R1, R16, R65, R66, R70, R95: 100K; R_0402_1005Metric
R2, R4, R5, R9, R13, R14, R19: 1K; R_0402_1005Metric
R3, R6: 4.99; R_0402_1005Metric
R8: 1; R_0402_1005Metric
R10, R15, R17, R87, R108, R109: 10K; R_0402_1005Metric
R11, R12: 1M; R_0402_1005Metric
R18: 470K; R_0402_1005Metric
R20: 0.02; R_0805_2012Metric
R72: 0.01; R_0402_1005Metric
R73: 0.01; R_1206_3216Metric
R76, R77, R81: 0; R_0402_1005Metric
R78, R79, R84, R114, R121: 10; R_0402_1005Metric
R86: 40.2K; R_0402_1005Metric
R92: 383K; R_0402_1005Metric
R93: 53.6K; R_0402_1005Metric
R94: 221K; R_0402_1005Metric
R98: 137K; R_0402_1005Metric
R99, R113: 30.1K; R_0402_1005Metric
TH1: 10K; R_0402_1005Metric
TP1: DSG_LED; TestPoint_Pad_1.0x1.0mm
TP2: BT1_LED; TestPoint_Pad_1.0x1.0mm
TP3: BT2_LED; TestPoint_Pad_1.0x1.0mm
TP4: BT3LED; TestPoint_Pad_1.0x1.0mm
TP5: BT4LED; TestPoint_Pad_1.0x1.0mm
U1: AP63205; TSOT-23-6
U2: TPS70933DBV; SOT-23-5
U3: BQ77915; TSSOP-24_4.4x7.8mm_P0.65mm
U4: BQ25703A_alt; Texas_S-PWQFN-N32_EP2.8x2.8mm_ThermalVias
U5: MSP430G2955IRHA40; Texas_S-PVQFN-N40_EP4.15x4.15mm

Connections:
+3.3VP: J9.7, Q10.2
+3V3: C7.2, C156.2, C157.2, J8.09, Q10.3, R65.2, R66.2, R108.1, R109.1, R113.2, U2.5, U5.14, U5.38, U5.39
+5V: C15.2, C16.2, J8.02, L1.2, U1.1
+BATT: 11.1.1, C119.2, C126.2, D2.2, R5.2, R9.2, R73.2, R79.2
-BATT: 0.0.1, C4.1, C5.2, C8.1, C9.2, R16.1, R17.1, R19.2, R20.2, TH1.1, U3.9, U3.10, U3.20, U3.23, U3.24
/A_EN: R70.2, U5.26
/BATDRVb: Q9.4, U4.21
/CHG_ACN: C114.2, C115.2, Q5.5, R3.2, R8.2, R72.1
/CHG_OK: R66.1, U4.4, U5.29
/CHG_PRC: R65.1, U4.11, U5.30
/CHG_SRN: R79.1, U4.19
/CHG_SRP: R78.1, U4.20
/COMP1: C140.2, R86.1, U4.16
/COMP2: C142.2, C144.2, U4.17
/DSG_EN: R1.1, U4.5, U5.12
/HB_HDV1: R76.2, U4.31
/HB_HDV2: R77.1, U4.24
/HB_HVDD1: C138.2, U4.30
/HB_HVDD2: C139.2, U4.25
/HB_LDV2: R81.1, U4.26
/HB_LG1: D5.1, Q4.1, U4.29
/HB_SW1: C138.1, L8.1, Q5.1, Q5.2, Q5.3, Q6.5, U4.32
/HB_SW2: C139.1, L8.2, Q7.1, Q7.2, Q7.3, Q8.5, U4.23
/IBAT: C153.2, U4.9, U5.7
/IPORT: C152.2, R98.2, U4.8, U5.6
/PSYS: R99.2, U4.10, U5.8
/REGN: C14.2, C151.2, Q4.3, R84.2, U4.28
/VDDA: C137.2, R84.1, R92.2, R93.2, U4.7
/VSYS: C120.1, C121.2, C122.2, C123.2, C124.2, Q7.5, Q9.5, U4.22
EN_3V3: Q10.1, U5.28
EN_5V0: U1.2, U5.40
EN_12V_G: R4.1, U5.3
EOC_KELLER: J8.05, J9.9
Earth: C1.1, C6.1, C7.1, C11.2, C12.1, C13.1, C14.1, C15.1, C16.1, C114.1, C115.1, C116.2, C120.2, C121.1, C122.1, C123.1, C124.1, C125.1, C126.1, C127.2, C128.2, C132.2, C135.2, C136.2, C137.1, C140.1, C142.1, C143.1, C151.1, C152.1, C153.1, C160.1, J8.01, J9.13, J9.14, NT2.2, Q1.3, Q3.3, Q6.1, Q6.2, Q6.3, Q8.1, Q8.2, Q8.3, R12.1, R18.1, R87.1, R98.1, R99.1, U1.4, U2.2, U4.14, U4.27, U4.33
GNDA: C156.1, C157.1, C161.1, C165.1, NT2.1, R1.2, R70.1, U5.1, U5.4, U5.13, U5.31, U5.41
GPS_INT: J8.07, J9.8
IMU_INT: J8.08, J9.10
unnamed: 3.4.1, R14.2
unnamed: 7.4_L1.1, R2.2
unnamed: 12V_OUT1.1, C1.2, C6.2, D1.1, D2.1, D3.1, U1.3, U2.1
unnamed: C2.1, R92.1, R94.2, U4.6
unnamed: C2.2, R94.1, R95.1
unnamed: C3.1, C4.2, R14.1, U3.7
unnamed: C5.1, R19.1, U3.8
unnamed: C8.2, R5.1, U3.1, U3.22
unnamed: C9.1, U3.2
unnamed: C10.1, L1.1, U1.5
unnamed: C10.2, U1.6
unnamed: C11.1, R3.1, U4.2
unnamed: C12.2, R6.1, U4.3
unnamed: C13.2, R8.1, U4.1
unnamed: C3.2, C17.1, R2.1, U3.6
unnamed: C17.2, R9.1, U3.3, U3.4, U3.5
unnamed: C119.1, C125.2, Q9.1, R73.1, R78.2
unnamed: C143.2, R86.2
unnamed: C144.1, R87.2
unnamed: D3.2, GND_OUT1.1, Q1.1
unnamed: D5.2, Q4.2, Q6.4
unnamed: Q1.2, R4.2
unnamed: Q2.1, Q3.1
unnamed: Q2.2, R10.1, R11.2
unnamed: Q2.3, R11.1, R20.1, U3.11
unnamed: Q3.2, R12.2, R13.1
unnamed: Q5.4, R76.1
unnamed: Q7.4, R77.2
unnamed: Q8.4, R81.2
unnamed: R10.2, U3.12
unnamed: R13.2, U3.13
unnamed: R15.1, TH1.2, U3.18
unnamed: R15.2, U3.19
unnamed: R16.2, U3.17
unnamed: R17.2, U3.16
unnamed: R18.2, U3.14
unnamed: R93.1, R95.2, U4.18
unnamed: R114.2, U5.11
unnamed: R121.2, U5.10
unnamed: TP1.1, U5.15
unnamed: TP2.1, U5.16
unnamed: TP3.1, U5.17
unnamed: TP4.1, U5.18
unnamed: TP5.1, U5.19
SBWTCK: J9.11, U5.37
SBWTDI: C160.2, J9.12, R113.1, U5.5
SCL: C161.2, J8.03, J9.5, R109.2, R114.1, U4.13
SDA: C165.2, J8.04, J9.6, R108.2, R121.1, U4.12
VBUS: C116.1, C127.1, C128.1, C132.1, C135.1, C136.1, D1.2, J9.1, J9.2, R6.2, R72.2
~INT~: J8.06, J9.3
~SHT_DWN_SIG~: J8.10, U5.36
~TS_EOC~: J9.4, U5.2

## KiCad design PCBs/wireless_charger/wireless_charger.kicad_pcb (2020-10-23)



Board: 4 copper layers, 65.0 x 69.5 mm, 116 parts (4 on the bottom side), 61 nets.

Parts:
C1, C2, C3, C4, C13, C15, C21, C26, C29, C30, C33, C34: 0.1uF; C_0402_1005Metric
C5, C14, C31, C37, C38, C40, C41: 10uF; C_0603_1608Metric
C6, C12, C16, C27: 1uF; C_0402_1005Metric
C7, C9: 56pF; C_0402_1005Metric
C8: 6.8nF; C_0402_1005Metric
C10, C11: 22nF; C_0603_1608Metric
C17: 680pF; C_0402_1005Metric
C18: 1nF; C_0603_1608Metric
C19, C35, C39: 5.6nF; C_0603_1608Metric
C20, C23, C24: 100nF; C_1206_3216Metric
C22: 22nF; C_0402_1005Metric
C25: 68nF; C_1206_3216Metric
C28, C32: 22uF; C_1206_3216Metric
C36, C46, C47: 10uF; C_0603_1608Metric_Pad1.05x0.95mm_HandSolder
C42: 0.1uF; C_0603_1608Metric
C43: 1uF; C_0603_1608Metric
C44: 4.7uF; C_0603_1608Metric
C45: 100nF; C_0603_1608Metric_Pad1.05x0.95mm_HandSolder
C48: 15pF; C_0402_1005Metric
CHG_LED1: GREEN; LED_0603_1608Metric
D1, D2: BAV21W; D_SOD-123
D3: MBR0530; D_SOD-123
FLT_LED1: RED; LED_0603_1608Metric
Fan_12V1: Conn_01x02; PinHeader_1x02_P2.54mm_Vertical
J1: Barrel_Jack_Switch; CUI_PJ-002AH
J2: Pi_Receiver; PinHeader_2x03_P2.54mm_Vertical
L1: 4.7uH; L_0603_1608Metric
L2: 4.7uH; L_1008_2520Metric
LX1, LX2: MountingHole_Pad; TestPoint_THTPad_D1.5mm_Drill0.7mm
Q1, Q2, Q3, Q4: DMG7430LFG; TRANS_DMP3017SFGQ-7_b
Q5, Q7, Q8: 2N7002; SOT-23
Q6: SiA453EDJ; Vishay_PowerPAK_SC70-6L_Single
Q9: NTR4003N; SOT-23
R1, R3, R7, R9: 1K; R_0402_1005Metric
R2, R5, R6, R13, R16, R19, R20, R22, R23, R41, R42, R43, R48: 10K; R_0402_1005Metric
R4: 680; R_0402_1005Metric
R8, R26, R30, R31, R32: 100K; R_0402_1005Metric
R10, R12: 390K; R_0603_1608Metric
R11, R35: 200K; R_0603_1608Metric
R14: 2.4K; R_0402_1005Metric
R15, R21: 10; R_0402_1005Metric
R17: 17.8; R_0402_1005Metric
R18: 0.02; R_0805_2012Metric
R25, R27, R28, R29: 12; R_0402_1005Metric
R33: 3; R_0805_2012Metric
R34: 100K; R_0603_1608Metric
R36, R37: 0.1; R_0402_1005Metric
R40: 14.3; R_0402_1005Metric
R44: 15.8K; R_0402_1005Metric
R45: 220; R_0805_2012Metric
TH1: 10K Thermistor; R_0805_2012Metric
U1: P9242-RNDGI8; QFN40P600X600X100-49N
U2: AP63205; TSOT-23-6
U3: LMV331; SOT-23-5

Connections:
+5V: C46.2, C47.2, J2.1, J2.3, L2.2, U2.1
/SCL: J2.6, R2.1, U1.15
/SDA: J2.4, R5.1, U1.16
/TS: C26.2, R20.2, TH1.1, U1.20, U3.1
/coil1: C11.2, C34.2, LX1.1, Q2.1, Q3.3, R30.1, U1.32
/coil2: C20.2, C23.2, C24.2, C25.2, C35.2, D1.2, LX2.1
Earth: C1.1, C2.2, C3.1, C4.1, C5.1, C6.1, C7.1, C9.1, C12.2, C13.1, C14.1, C15.1, C16.1, C17.1, C18.1, C19.1, C21.1, C26.1, C28.1, C29.1, C30.1, C31.1, C32.1, C36.1, C37.1, C38.1, C39.1, C40.1, C41.1, C42.2, C43.2, C44.2, C46.1, C47.1, C48.1, J1.2, J1.3, J2.5, Q3.1, Q4.1, Q5.2, Q7.2, Q8.2, Q9.2, R7.2, R8.1, R11.2, R12.2, R19.1, R31.1, R32.1, R34.2, R36.1, R37.1, R40.1, R44.1, TH1.2, U1.2, U1.6, U1.34, U1.41, U1.49, U2.4, U3.2
ISNS_H: C27.1, R15.1, U1.48
ISNS_L: C27.2, R21.1, U1.47
LDO18: C6.2, C13.2, U1.9
LDO33: C16.2, C21.2, CHG_LED1.2, FLT_LED1.2, R2.2, R5.2, R17.2, R20.1, R22.1, R23.2, R35.2, R43.2, R48.2, U1.7, U1.12, U3.5
unnamed: C1.2, C37.2, C40.2, Q2.3, Q6.1, R33.2, R45.1
unnamed: C7.2, C8.2, U1.45
unnamed: C8.1, R6.1
unnamed: C9.2, R6.2, U1.46
unnamed: C10.1, R37.2
unnamed: C10.2, C20.1, C23.1, C24.1, C25.1, C33.2, Q1.1, Q4.3, R26.1, U1.36
unnamed: C11.1, R36.2
unnamed: C12.1, U1.3
unnamed: C17.2, C22.1, U1.44
unnamed: C19.2, R11.1, R13.2, R14.1
unnamed: C22.2, R13.1
unnamed: C3.2, C29.2, C38.2, C41.2, Q1.3, Q6.4, R18.1, R21.2, R42.2, R45.2, U1.40
unnamed: C33.1, U1.37
unnamed: C34.1, U1.31
unnamed: C35.1, D2.2, R34.1, R35.1
unnamed: C39.2, R1.1, R10.1, R12.1
unnamed: C45.1, L2.1, U2.5
unnamed: C45.2, U2.6
unnamed: C48.2, R9.1, R22.2, U3.4
unnamed: CHG_LED1.1, R4.2
unnamed: D1.1, R14.2
unnamed: D2.1, R1.2
unnamed: D3.2, Fan_12V1.1, Q9.3
unnamed: FLT_LED1.1, R3.2
unnamed: L1.2, U1.5
unnamed: Q1.2, R25.1, R26.2
unnamed: Q2.2, R29.1, R30.2
unnamed: Q3.2, R28.1, R31.2
unnamed: Q4.2, R27.1, R32.2
unnamed: Q5.3, R33.1
unnamed: Q6.3, R41.2, R42.1
unnamed: Q7.3, R41.1
unnamed: Q8.3, R16.2
unnamed: Q9.1, R9.2
unnamed: R3.1, U1.10
unnamed: R4.1, U1.11
unnamed: R7.1, U1.1
unnamed: R17.1, R19.2, U3.3
unnamed: R25.2, U1.38
unnamed: R27.2, U1.35
unnamed: R28.2, U1.33
unnamed: R29.2, U1.30
unnamed: R40.2, R48.1, U1.17
unnamed: R43.1, R44.2, U1.18
OVP_CTL: Q8.1, U1.22
Q_DRV1: Q5.1, R8.2, U1.23
Q_DRV2: Q7.1, R23.1, U1.24
VCC_5V: C4.2, C5.2, C30.2, C31.2, L1.1, U1.8, U1.39
VCOIL_OV: C18.2, R10.2, R16.1, U1.19
VIN: C2.1, C14.2, C15.2, C28.2, C32.2, C36.2, C42.1, C43.1, C44.1, D3.1, Fan_12V1.2, J1.1, R15.2, R18.2, U1.4, U2.2, U2.3

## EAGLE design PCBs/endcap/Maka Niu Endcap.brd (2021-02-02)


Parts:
BATT_CONNECT: MOLEX_87759_1450; 87759-1450; DIGI-KEY_PART_NUMBER WM18654-ND
C1: 33nF/50V; C0402; DIGI-KEY_PART_NUMBER 490-13296-1-ND
C2, C3, C5: 22nF/50V; C0402; DIGI-KEY_PART_NUMBER 490-6360-1-ND
C4, C12, C13, C15, C18, C20, C24: 1uF; C0402; DIGI-KEY_PART_NUMBER 311-1439-1-ND
C6, C14: 47nF; C0402; DIGI-KEY_PART_NUMBER 490-10702-1-ND
C7, C17, C26: 0.1uF; C0402; DIGI-KEY_PART_NUMBER 490-11917-1-ND
C8, C16: 15nF; C0402; DIGI-KEY_PART_NUMBER 490-16428-1-ND
C9: 1nF; C0402; DIGI-KEY_PART_NUMBER 732-7556-1-ND
C10, C11, C21, C22, C33: 10uF; C_0603; DIGI-KEY_PART_NUMBER 445-9015-1-ND
C19, C31: 0.1uF; C0201; DIGI-KEY_PART_NUMBER 445-7318-1-ND
C23: 0.1uF; C0201; DIGI-KEY_PART_NUMBER 1276-1318-1-ND
COIL: CHARGING_COIL
D2: 0.5A/40V/420mV; SOD-323; DIGI-KEY_PART_NUMBER 1727-5209-1-ND
FB1: 600Ω/100MHz; 0603; DIGI-KEY_PART_NUMBER 445-172898-1-ND
J1: U.FL; DIGI-KEY_PART_NUMBER A144746CT-ND
J2: KELLER_BREAKOUT; WIRES_2MM_05
J3: GPS_PROG; WIRES_2MM_02SMD
L1: 33nH/±5%/500mA; 0603; DIGI-KEY_PART_NUMBER 490-14837-1-ND
Q1, Q2: 20V/0.2A/8MHz/1.2Ω/1Vth; SOT-416FL; DIGI-KEY_PART_NUMBER RE1C002UNTCLCT-ND
R1, R3: 470; R0402; DIGI-KEY_PART_NUMBER RMCF0402JT470RCT-ND
R2: 36; R0805; DIGI-KEY_PART_NUMBER P36ADCT-ND
R4: 1k; R0402; DIGI-KEY_PART_NUMBER RMCF0402JT1K00CT-ND
R5, R6, R7, R8: 4.7k; R0402; DIGI-KEY_PART_NUMBER RMCF0402JT4K70CT-ND
R9, R10: 10k; R0402; DIGI-KEY_PART_NUMBER RMCF0402JT10K0CT-ND
R13, R14: 5.1k; R0402; DIGI-KEY_PART_NUMBER CR0402-JW-512GLFCT-ND
R15, R16: 10k; R_0603; DIGI-KEY_PART_NUMBER 311-10.0KHRCT-ND
R17, R19, R23, R27, R29, R34, R38, R39: 10k; R0402; DIGI-KEY_PART_NUMBER 541-10KATCT-ND
R22, R28, R30: NP; R0402
R33: 39.2k; R0402; DIGI-KEY_PART_NUMBER 311-39.2KLBCT-ND
RTS: THERMISTOR-2,5; RS-2,5
TP1: TP_18V; B1,27
TP2: TP_GND; B1,27
U1: P9221-R03MM_PAD; CSP52_2P64X3P94_0P4MM_03MMPAD; DIGI-KEY_PART_NUMBER 800-3932-2-ND
U2: XM1110 GPS; XM1110_GPS; DIGI-KEY_PART_NUMBER 1645-XM1110_1104311CT-ND
U3: ICM-20948; QFN40P300X300X105-24N
U4: 1.8V/100mA; SC70; DIGI-KEY_PART_NUMBER 576-2807-1-ND

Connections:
1.8V: C24.1, C26.1, Q1.1 (G), Q2.1 (G), R7.2, R8.2, TP1.TP, U3.8 (VDDIO), U3.13 (VDD), U3.22 (NCS), U4.5 (OUT)
3VBATT: BATT_CONNECT.12, D2.A
!INT: BATT_CONNECT.3, R23.1, U1.C3 (!INT)
+3V3: BATT_CONNECT.7, C12.1, C15.1, FB1.1, J2.1, L1.1, R5.2, R6.2, R9.2, R10.2, U4.1 (IN), U4.3 (EN)
AC1: C1.2, C2.2, C3.2, C5.2, C6.1, C8.1, C9.1, U1.G2 (AC1), U1.H1 (AC1_1), U1.H2 (AC1_2)
AC2: C9.2, C14.1, C16.1, COIL.B2 (2), U1.G5 (AC2), U1.H5 (AC2_1), U1.H6 (AC2_2)
ALIGNX: R16.1, U1.A2 (ALIGNX)
ALIGNY: R15.1, U1.B2 (ALIGNY)
BST1: C8.2, U1.G1 (BST1)
BST2: C16.2, U1.G6 (BST2)
COMM1: C6.2, U1.A1 (COMM1)
COMM2: C14.2, U1.A6 (COMM2)
DEN: R39.1, U1.C5 (DEN)
EOC: BATT_CONNECT.9, J2.4
GND: BATT_CONNECT.13, BATT_CONNECT.14, C4.2, C7.2, C10.2, C11.2, C12.2, C13.2, C15.2, C17.2, C18.2, C19.2, C20.2, C21.2, C22.2, C23.2, C24.2, C26.2, C31.2, C33.2, J1.1 (GND), J1.2 (GND), J2.5, R15.2, R16.2, R17.2, R22.1, R27.1, R29.1, R33.1, RTS.2, TP2.TP, U1.C1 (PGND), U1.C6 (PGND1), U1.J1 (PGND2), U1.J2 (PGND3), U1.J3 (PGND4), U1.J4 (PGND5), U1.J5 (PGND6), U1.J6 (PGND7), U2.1 (GND), U2.3 (GND), U2.4 (GND), U2.5 (GND), U2.6 (GND), U2.9 (GND), U3.11 (FSYNC), U3.18 (GND), U3.20 (RESV_20), U4.2 (GND)
GPS_INT: BATT_CONNECT.8, U2.13 (INT)
ILIM: R22.2, R38.1, U1.B4 (ILIM)
IMU_INT: BATT_CONNECT.10, U3.12 (INT1)
LC: C1.1, C2.1, C3.1, C5.1, COIL.B1 (1)
unnamed: R17.1, U1.B5 (!EN)
unnamed: D2.C, R4.2
REGOUT: C17.1, U3.10 (REGOUT)
RF_IN: J1.FEED (SIGNAL), L1.2, U2.2 (RF_IN)
RPPG: R27.2, R28.1, U1.A5 (RPPG)
RPPO: R29.2, R30.1, U1.C4 (RPPO)
RX: J3.2, R1.2, R9.1
RX0: R1.1, U2.17 (RX0)
SCL: BATT_CONNECT.5, J2.3, Q2.3 (D), R6.1, R13.1, U1.A3 (SCL), U2.11 (I2C_SCL)
SCL/SCLK: Q2.2 (S), R8.1, U3.23 (SCL/SCLK)
SDA: BATT_CONNECT.6, J2.2, Q1.3 (D), R5.1, R14.1, U1.B3 (SDA), U2.10 (I2C_SDA)
SDA/SDI: Q1.2 (S), R7.1, U3.24 (SDA/SDI)
SINK: R2.1, U1.C2 (SINK)
TS/EOC: BATT_CONNECT.4, C31.1, R19.1, RTS.1, U1.H4 (TS)
TX: J3.1, R3.2, R10.1
TX0: R3.1, U2.16 (TX0)
VBACKUP: C13.1, R4.1, U2.8 (VBACKUP)
VCC: C4.1, C7.1, FB1.2, U2.7 (VCC)
VDD5V: C18.1, U1.F1 (VDD5V)
VDD18: C19.1, C20.1, R13.2, R14.2, R19.2, R23.2, R28.2, R30.2, R34.2, R38.2, R39.2, U1.F6 (VDD18)
VOSET: R33.2, R34.1, U1.A4 (VOSET)
VOUT: BATT_CONNECT.1, BATT_CONNECT.2, C10.1, C11.1, U1.D1 (OUT), U1.D2 (OUT1), U1.D3 (OUT2), U1.D4 (OUT3), U1.D5 (OUT4), U1.D6 (OUT5), U1.G3 (RSV3), U1.H3 (RSV2)
VRECT: C21.1, C22.1, C23.1, C33.1, R2.2, U1.E1 (VRECT), U1.E2 (VRECT1), U1.E5 (VRECT2), U1.E6 (VRECT3), U1.F2 (VRECT4), U1.F3 (VRECT5), U1.F4 (VRECT6), U1.F5 (VRECT7)



Board: 6 copper layers, 26.0 x 26.0 mm, 70 parts (28 on the bottom side), 42 nets.

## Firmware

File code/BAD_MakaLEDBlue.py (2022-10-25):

#!/usr/bin/sudo /usr/bin/python3
import logging
import logging.handlers
import glob
import datetime
import time
from time import sleep
import os
import RPi.GPIO as GPIO
import array as arr
import sys
import subprocess
from subprocess import call #, PIPE, Popen
import board
import busio
from kellerLD import KellerLD
import socket
import re, uuid
import pigpio
import wavePWM
from bluedot.btcomm import BluetoothServer

#from gpiozero import CPUTemperature



def get_cpu_temperature():
   try:
      tFile = open('/sys/class/thermal/thermal_zone0/temp')
      temp = float(tFile.read())/1000.0
      return temp
   except:
      return 0

def data_received(data):
   #print(data)
   try:
      light_duration = str2num(data)
      camera_module.send("OK: " + data)
   except:
      light_duration = 0
      camera_module.send("Sorry, what?")


#############################################################SETUP ERROR AND DEBUG LOGGING
#name of the next log file
LOG_FILENAME = '/home/pi/git/maka-niu/code/log/MakaLED_debug.log'

#create logging objects
logger = logging.getLogger('MyLogger')
logger.setLevel(logging.DEBUG)

#setup up to 0 backup log files, meaning we keep logs of last 10 runtimes
handler = logging.handlers.RotatingFileHandler(LOG_FILENAME, backupCount = 9)
logger.addHandler(handler)

#determine if any log file exist and if yes all existing logs need to rolloverm then print the list
needRoll = os.path.isfile(LOG_FILENAME)
if needRoll:
   logger.handlers[0].doRollover()

#and now make all debug message also print to console
logger.addHandler(logging.StreamHandler(sys.stdout))


############################################################### SETUP
#control variables: change these as desired
mac_address = ':'.join(re.findall('..', '%012x' % uuid.getnode()))
serial_number = socket.gethostname()
hdmi_act_led_timeout_seconds = 90
battery_low_shutdown_timeout_seconds = 60
light_timelimit_seconds = 900 # 15 minutes


mission1_name = 'M1'
mission2_name = 'M2'
#To avoid messing with pi's clock, we are creating a UTC datetime offset variable that will be used for timestamping filenames and sensor data
datetime_offset = datetime.timedelta(0)

#print code version, date time and unit serial number
version = subprocess.check_output(["git", "describe", "--always"], cwd=os.path.dirname(os.path.abspath(__file__))).strip().decode()
logger.debug("Serial number: {}\tPi datetime: {}\tMAC: {}\tCode versin: {}".format(serial_number, datetime.datetime.now(), mac_address, version))
with open('/home/pi/git/maka-niu/code/log/version.txt', 'w') as f:
   print("{}".format(version), end="", file=f, flush= True)


#setup a timer to disable HDMI output, that way for debug it is still possible to connect a screen and end this program before hdmi cuts.
hdmi_end_timer = time.time()
hdmi_enabled = True

#setup LED pwms pins for feedback
GPIO.setmode(GPIO.BCM)

#setup the GPIO pin that enables 3.3V regulator in the BMS board that powers GPS, Keller, IMU.
GPIO.setup(18, GPIO.OUT)
GPIO.output(18, GPIO.HIGH) #NOTE: is a mission has long standby time and the peripherals are not needed, one may set this pin low to preserve power
sleep(0.5)

#setup SPI for battery ADC via MCP3002 and a 100K/33K voltage divider on the battery pack voltage
#If there is a hardware issue, flag it and do not use the feature anymore this runtime.
battery_low_counter = 0
battery_volt = 12
adc_connected = True
try:
   i2c = busio.I2C(board.SCL, board.SDA)
   result = bytearray(2)

   i2c.readfrom_into(0x4e, result)
   battery_volt = ((result[0] <<8 | result[1]) & 0xFFF) * 0.003223
   #: 3.3Vref / 4095(12bit) * 4(voltage_divide) = 0.003223
   logger.debug("Starting battery voltage: {}V".format(round(battery_volt,3)))

except:
   logger.error("ADC not connected, SPI Exception")
   adc_connected = False



if battery_volt < 5 or battery_volt > 15:
   logger.debug("ADC not connected, values out of range.")
   adc_connected = False
   battery_volt = 12

#If the batteries are already depleted at start of runtime, initiate shutdown with a timeout to allow for user to intercept
if battery_volt < 9.0:
   logger.debug('Batteries critically low, initiating shutdown in 60 seconds.')
   sys.stdout.flush()

   sleep(battery_low_shutdown_timeout_seconds)
   GPIO.cleanup()
   call("sudo shutdown -h now", shell=True)
   sys.exit()


#setup i2c for keller pressure/temperature sensor
#If there is a hardware issue, flag it and do not use the feature anymore this runtime.
outside = KellerLD()
keller_connected = True
try:
   outside.init()
   logger.debug("Keller sensor connected")

except:
   keller_connected = False
   logger.error("Keller LD sensor not connected. Exception")

#setup i2c for IMU sensor
#If there is a hardware issue, flag it and do not use the feature anymore this runtime.
imu_connected = True
try:
   imu = qwiic_icm20948.QwiicIcm20948()
   if imu.connected == False:
      imu_connected = False
      logger.error("IMU sensor not connected")
   else:
      imu.begin()
      imu.setFullScaleRangeAccel(0x02) #+-8G forces
      imu.setFullScaleRangeGyro(0x00) #250 degrees per second
      logger.debug("IMU sensor connected")
except:
   imu_connected = False
   logger.error("IMU sensor not connected. Exception")

light_duration = 0
light_request_time = time.time()
bluetooth_server_running = False
try:
   camera.module = BluetoothServer(data_received)
   logger.debug("Bluetooth server setup")
   bluetooth_server_running = True
except:
   logger.error("Bluetooth server fail")



#setup hall sensor GPIO pins. All pulled up, so active is when low
GPIO.setup(8, GPIO.IN, pull_up_down = GPIO.PUD_UP)  #push button
GPIO.setup(11, GPIO.IN, pull_up_down = GPIO.PUD_UP) #wifi mode
GPIO.setup(25, GPIO.IN, pull_up_down = GPIO.PUD_UP) #video mode
GPIO.setup(9, GPIO.IN, pull_up_down = GPIO.PUD_UP)  #photo mode
GPIO.setup(24, GPIO.IN, pull_up_down = GPIO.PUD_UP) #mission 2 mode
GPIO.setup(10, GPIO.IN, pull_up_down = GPIO.PUD_UP) #mission 1 mode
GPIO.setup(14, GPIO.IN, pull_up_down = GPIO.PUD_UP) #power down signal

#hall dial variables
hall_button_active = 0
hall_button_last = 0
hall_active = arr.array('i', [0,0,0,0,0,0]) #binary active or not
hall_confidence = arr.array('i', [0,0,0,0,0,0]) #gradient confidence
hall_most_confident_value =0
hall_mode = 0
hall_mode_last = 0

#other variables
recording = 0 #when recording, this flag is set so that modes changes are limited /prevented
end_processes_mode_changed_flag = 0 #flag to properly end videos and sensor data files when mode changes
photo_burst_time = time.time() #to manage time delay between images in burst
interface_rotation = 0 #alternate various i2c jobs and battery spi job to minimize delay
light_started_time = time.time() # for limiting video to fixed max lentgh segments
interfaces_time = time.time() # for timing interface comms
in_mission =0 # either not in a mission, or in mission 1 or 2.
fix_time_stamp= time.time()
fix_achieved_this_runtime = False
fix_is_live = False
fix_latitude = 0.0
fix_longitude = 0.0
fix_last_UTC_update = datetime.datetime.now()
gnss_string = ""
batt_string = ""
kell_string = ""
imu_string = ""
clock_updated_this_runtime = False
wifi_enabled = True

gps_connected = False
haptic_connected = False

#setup keller depth offset calibration
approx_depth = 0
keller_depth_offset = 0
if os.path.exists('/home/pi/git/maka-niu/code/log/keller_offset.txt'):
   k = open('/home/pi/git/maka-niu/code/log/keller_offset.txt', 'r')
   depth_string = k.readline()
   keller_depth_offset = float(depth_string)
   k.close()
   logger.debug('Initial keller depth offset of {} loaded.'.format(keller_depth_offset))


#If all the hardware interfaces appear to be functioning, turn the green len on for 3 seconds
#if adc_connected and gps_connected and keller_connected:
#   logger.debug('??? hardware all talking.')
#   sleep(3)

#Print to stream that setup is over
logger.debug('Maka LED Program setup complete Entering main forever loop.')


pi=pigpio.pi()
light = wavePWM.PWM(pi)
light.set_frequency(1000)

target_brightness = 0
duty_cycle = target_brightness
light.set_pulse_length_in_fraction(13, duty_cycle)
light.update()


#light.cancel()
#pi.stop()
#exit(0)
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

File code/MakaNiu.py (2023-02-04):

#!/usr/bin/sudo /usr/bin/python3
import logging
import logging.handlers
import glob
import datetime
import time
from time import sleep
import os
import RPi.GPIO as GPIO
import array as arr
import sys
import subprocess
from subprocess import call
import board
import busio
import adafruit_drv2605
import spidev
import qwiic_titan_gps
import qwiic_icm20948
from kellerLD import KellerLD
import socket
import re, uuid
import pigpio
import wavePWM
import math
from bluedot.btcomm import BluetoothClient
from bluedot.btcomm import BluetoothAdapter


#############################################################SETUP ERROR AND DEBUG LOGGING
#name of the next log file
LOG_FILENAME = '/home/pi/git/maka-niu/code/log/MakaNiu_debug.log'

#create logging objects
logger = logging.getLogger('MyLogger')
logger.setLevel(logging.DEBUG)

#setup up to 0 backup log files, meaning we keep logs of last 10 runtimes
handler = logging.handlers.RotatingFileHandler(LOG_FILENAME, backupCount = 9)
logger.addHandler(handler)

#determine if any log file exist and if yes all existing logs need to rolloverm then print the list
needRoll = os.path.isfile(LOG_FILENAME)
if needRoll:
   logger.handlers[0].doRollover()

#and now make all debug message also print to console
logger.addHandler(logging.StreamHandler(sys.stdout))


############################################################### SETUP

#control variables: change these as desired
mac_address = ':'.join(re.findall('..', '%012x' % uuid.getnode()))
serial_number = socket.gethostname()
mission1_name = "M1" #can be user specified
mission2_name = "M2" #can be user specified
hdmi_act_led_timeout_seconds = 90
battery_low_shutdown_timeout_seconds = 60
video_timelimit_seconds = 900 # 15 minutes


#Due to changes in hardware, need to know which generation of hardware we are on
#version can be undefined (original) and we set to 0, or it can be 1, 2 3, etc
if os.path.exists('/home/pi/git/maka-niu/code/log/hardware_version.txt'):
   with open('/home/pi/git/maka-niu/code/log/hardware_version.txt', 'r+') as k:
      try:
         hardware_string = k.readline()
         hardware_version = int(hardware_string)
         logger.debug('hardware version is {}'.format(hardware_string))

      except:
         hardware_version = 0
         k.seek(0)
         print("{}".format(hardware_version) , end="", file=k, flush= True)
         k.truncate()
         logger.error("Error reading hardware version. Wrote 0 to version file")
else:
   hardware_version = 0


############################################################### FUNCTIONS
if hardware_version == 0:
   def getBatteryVoltage(vref = 3.3):
      msg = 0b11
      msg = ((msg << 1) + 0) << 5
      msg = [msg, 0b00000000]
      reply = spi.xfer2(msg)
      adc = 0
      for n in reply:
         adc = (adc << 8) + n
      adc = adc >> 1
      voltage = (vref * adc)/1024
      pack_voltage = voltage * 4 + 0.3 # adc * voltage + plus diode forward drop
      return pack_voltage

elif hardware_version == 1:
   def getBatteryVoltage():
      result = bytearray(2)
      i2c.readfrom_into(0x4e,result)
      voltage = ((result[0] <<8 | result[1]) & 0xFFF) * 0.003223
      #: 3.3Vref / 4095(12bit) * (voltage_divider in hardware) = 0.003223
      return voltage

#bluetooth function
def data_received(data):
   logger.debug("BLUE:{}\n".format(data))



#To avoid messing with pi's clock, we are creating a UTC datetime offset variable that will be used for timestamping filenames and sensor data
datetime_offset = datetime.timedelta(0)

#print code version, date time and unit serial number
version = subprocess.check_output(["git", "describe", "--always"], cwd=os.path.dirname(os.path.abspath(__file__))).strip().decode()
logger.debug("Serial number: {}\tPi datetime: {}\tMAC: {}\tCode versin: {}".format(serial_number, datetime.datetime.now(), mac_address, version))
with open('/home/pi/git/maka-niu/code/log/version.txt', 'w') as f:
   print("{}".format(version), end="", file=f, flush= True)

#setup a timer to disable HDMI output, that way for debug it is still possible to connect a screen and end this program before hdmi cuts.
hdmi_end_timer = time.time()
hdmi_enabled = True


if hardware_version ==0:
   #setup LED pwms pins for feedback
   GPIO.setmode(GPIO.BCM)
   GPIO.setup(12, GPIO.OUT)
   GPIO.setup(13, GPIO.OUT)

   #define ledOn/ledOff with fixed PWM intensity, since we moved away from fades
   def redOn():   GPIO.output(12,GPIO.HIGH)
   def redOff():   GPIO.output(12,GPIO.LOW)
   def greenOn():   GPIO.output(13,GPIO.HIGH)
   def greenOff():   GPIO.output(13,GPIO.LOW)

   #define buzzer function as pass, since  hardware 0 does not have a buzzer
   def clickSound(): pass
   def clickSoundSingle(): pass
   def buzFadeOn(): sleep(0.325)
   def buzOn(): pass
   def buzOff(): pass
   def buzFadeOff(): sleep(0.325)


elif hardware_version ==1:
   #chooze naming convention
   GPIO.setmode(GPIO.BCM)

   #setup LED pins
   GPIO.setup(5, GPIO.OUT)
   GPIO.setup(6, GPIO.OUT)
   #set up blink functions
   def redOn():   GPIO.output(5,GPIO.HIGH)
   def redOff():   GPIO.output(5,GPIO.LOW)
   def greenOn():   GPIO.output(6,GPIO.HIGH)
   def greenOff():   GPIO.output(6,GPIO.LOW)

   #setup audio pins 12 and 13. 13 will be driven with PWM using pigpio process, 12 will just be pulled to ground.
   GPIO.setup(12, GPIO.IN, pull_up_down = GPIO.PUD_DOWN) #buzzer low side, also physically wired to ground

   #setup pigpiod
#   call("sudo pigpiod", shell=True)
   sleep(0.5)
#   pi = pigpio.pi()
#   buzzer = wavePWM.PWM(pi)
   buz_volume = 1.0 #this is pulse width out of 1, so not at all the same as dB now really a 0to1 sound bar
   buz_start_freq = 1000
   buz_end_freq = 2000
   sweep =  buz_end_freq - buz_start_freq


   def clickSoundSingle(): pass
#      buzzer.set_frequency(buz_start_freq)
#      half_cycle_width = buzzer.get_cycle_length()/2*buz_volume
#      buzzer.set_pulse_start_and_length_in_micros(13,half_cycle_width,half_cycle_width)
#      buzzer.update()
#      sleep(0.05)
#      buzzer.set_pulse_start_and_length_in_micros(13,0,0)
#      buzzer.update()

   def clickSound(): pass
#      buzzer.set_frequency(buz_start_freq)
#      half_cycle_width = buzzer.get_cycle_length()/2*buz_volume
#      buzzer.set_pulse_start_and_length_in_micros(13,half_cycle_width,half_cycle_width)
#      buzzer.update()

#      sleep(0.05)
#      buzzer.set_frequency(buz_end_freq)
#      half_cycle_width = buzzer.get_cycle_length()/2*buz_volume
#      buzzer.set_pulse_start_and_length_in_micros(13,half_cycle_width,half_cycle_width)
#      buzzer.update()
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

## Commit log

2020-06-24 Lui's first commit, addign a python script to record video on the Pi Zero with aa camera module, with timestamp overlay. This could be used in Maka Niu to overlay temperature, depth etc. Also adding 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
2020-07-13 added the kellerLD library, and a version of the example with a depth estimation based on pressure.
2020-07-17 Added a more complex python program Mode_dial_with_button for testing the the new hall sensor ring togethr with the new dial lthat incorporates a button
2020-08-13 Added the hall ring magnetic dial Kicad project
    [Hall_ring.kicad_pcb, Hall_ring.sch]
2020-08-13 added the battery management board kicad project
    [Maka_BMS.kicad_pcb, Maka_BMS.sch]
2020-08-13 Icreased trace thickness and rerouted higher freq and power paths in the battery management board
    [Maka_BMS.kicad_pcb, Maka_BMS.sch]
2020-08-14 added documenation folder and pushed 1st Power Distribution Chart
2020-08-14 changed current sensing resistor values on the BMS board to appropriately trip short and over current situations, adn to appropriately end incomig charge
    [Maka_BMS.sch]
2020-08-18 assigned digikey part to every item in battery management schematic, and created BOM
    [Maka_BMS.csv, Maka_BMS.sch]
2020-09-03 adding in progress pcb design files for the charging Station
    [charger_outline.dxf, wireless_charger.kicad_pcb, wireless_charger.sch]
2020-09-22 completed the wireless charger PCB design as rev 0. bom is compiled
    [Maka_BMS.sch, charger_outline_large.dxf, wireless_charger.csv, wireless_charger.kicad_pcb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]
2020-09-25 minor updating on BOM organization
    [wireless_charger.kicad_pcb]
2020-10-02 adding LED patterns simplified.
2020-10-23 added makaniu BMS board V2, and wayfinders 6cell BMS.
    [Hall_ring.sch, Maka_BMS.csv, Maka_BMS.kicad_pcb, Maka_BMS.sch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]
2020-11-22 updates to battery managemennt wayfinder boards, and makaniu hall sensor ring and BMS
    [Hall_ring.csv, Hall_ring.kicad_pcb, Hall_ring.sch, Maka_BMS.csv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]
2020-12-04 Minor notes on BMS pcb project
    [Maka_BMS.sch]
2020-12-04 added Maka Niu User Flowchart.pdf in documentation
2021-01-15 commented out drv vibration code because it causes crash if device not present
2021-01-18 MakaNiu.py program updated to include pressure info, as well as battery info, although it is disabled due to instability
2021-01-18 Lengthened update time for GPS and pressure to once every ten seconds, so that it interferes less with button presses. Need to bring in threads maybe, thou mixing I2c is scary. Also added a program t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
2021-01-22 All interfaces now protected with try/except method to prevent crashes. Program will run if any of these are missing. If all is present and talking, at startup, a green LED will hold for 3 seconds. A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
2021-01-25 Due to a a sepcific startup issue that emerged with introduciton of spi1, the shutdown pin has been switched with the enable endcap pin. Also added the enable endcap feature.
2021-02-02 Add files via upload
    Silkscreen modified for production
    [Maka Niu Endcap.brd]
2021-02-02 Add files via upload
    Finalized for production
    [Maka Niu Endcap.sch]
2021-02-02 Add files via upload
    added documentation for endcap PCB
2021-02-12 added sensor data file creation for videos
2021-02-13 added sensor data saving for images and burst images. Addressed a bug where burst photos also start a video.
2021-02-15 Added system clock entry in the sensor data files so that the separate mission manager program can easily read entry time
2021-02-18 Added IMU sensor data collection and write to sensor files
2021-02-19 added battery power indication in wifi mode when battery pressed
2021-02-22 removed import of makaniu_config.py for now, not currently used
2021-02-22 sensor file writing now has has flush built into every print to update the files faster, and mode changes are written to a status file in log directory for easy read by other running software
2021-02-23 software/hardware fix of imu address bug. pin address was floating in hardware, so hardware fix sets the address to 0x69. Software follows the correction
2021-02-24 fixed datestamp for special case gns2 data in photo captures
2021-02-25 updated the repo with all latest pcb changes for the 6cell bms, 3cell bms, and for the wireless charger. Also added sensor data readme filein the same directory as the makaniu python program
    [Maka_BMS.kicad_pcb, Maka_BMS.sch, wireless_charger.sch]
2021-04-04 disabled led and hdmi cuttoff after some time, till this feature is really needed feo deployment
2021-04-08 added device id and mac address data to the top of each generated sensor file
2021-05-21 hacked in support for uploading attachments
2021-05-21 added link to attachments upload tutorial
2021-05-26 Reinstated LED and HDMI shutdown for poer saving, and reduced burst photo rate to 2hz to sidestep a bug that caused missing thumbnail images
2021-07-08 implemented keller depth offset background calibration that uses gps fix as reference for 0 depth.
2021-07-08 implemented clock update from gps even without a fix. Also disabled wifi in non wifi modes for power saving
2021-11-17 code version print changed to 1.03, to make it a little easier to track if users are up to date
2021-12-10 added a dimmensioned drawing of the Maka Niu Housing in the documentation section
    [Maka_BMS.sch]
2021-12-11 minor correction to a dimenisions pdf drawing of the enclosure
2022-01-29 makaniu.py has minor edits. big one is keeping wifi enabled in non wifi mode if camera is believed to be above water
2022-02-01 removed outdated battery manager schematic
2022-02-01 changed voltage ranges for feedback so that the full charge 5 flashes are more likely to show on a full charge
2022-02-02 revised battery level visual feedback threshold voltages again based on observed voltage over time for a full charge to full deplete mission
2022-02-14 implemeted basic verion printing with incremented commits
2022-02-14 corrected bug on version printing when the daemon is called from outside the git repo, such as on boot
2022-06-15 added new pcb projects: hall_ring, pi_zero_shield, and batter_manager_V1.1
    [Hall_ring.csv, Hall_ring.kicad_pcb, Hall_ring.sch, Maka_BMS.kicad_pcb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]
2022-07-05 number of PCBs for 2nd round of Maka Niu fabrication, in their state after orders made.
    [Cree LED XLamp XHP50.2.STEP, Hall_ring.csv, Hall_ring.kicad_pcb, Hall_ring.kicad_sch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]
2022-07-07 added a code sample for a great passive buzzer controller
2022-07-29 added beginnig of MakaNiu LED ligth code with quality PWM control
2022-08-05 added battery reading to MakaLED.py
2022-08-05 added battery level coutn in wifi button press for the flashlight code
2022-10-25 added bluettooth LED module code. Still testing
2022-11-19 corrected IP address for LED version
2023-01-16 changed audio frequency to be audible outside of housing
2023-01-19 added method for Maka Niu to control LED module over bluetooth. An initial connection between two units must still be done manually over command line once, but afterwards units can be rebooted and th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
2023-01-19 cleaned up the LED module code quite a bit, removing some undefined/unusued variables, making it much more stable
2023-01-19 revised how to retrieve bluetooth device name and address to. It now gets it diretly from the bluetooth hardware, rather than from a manual text file

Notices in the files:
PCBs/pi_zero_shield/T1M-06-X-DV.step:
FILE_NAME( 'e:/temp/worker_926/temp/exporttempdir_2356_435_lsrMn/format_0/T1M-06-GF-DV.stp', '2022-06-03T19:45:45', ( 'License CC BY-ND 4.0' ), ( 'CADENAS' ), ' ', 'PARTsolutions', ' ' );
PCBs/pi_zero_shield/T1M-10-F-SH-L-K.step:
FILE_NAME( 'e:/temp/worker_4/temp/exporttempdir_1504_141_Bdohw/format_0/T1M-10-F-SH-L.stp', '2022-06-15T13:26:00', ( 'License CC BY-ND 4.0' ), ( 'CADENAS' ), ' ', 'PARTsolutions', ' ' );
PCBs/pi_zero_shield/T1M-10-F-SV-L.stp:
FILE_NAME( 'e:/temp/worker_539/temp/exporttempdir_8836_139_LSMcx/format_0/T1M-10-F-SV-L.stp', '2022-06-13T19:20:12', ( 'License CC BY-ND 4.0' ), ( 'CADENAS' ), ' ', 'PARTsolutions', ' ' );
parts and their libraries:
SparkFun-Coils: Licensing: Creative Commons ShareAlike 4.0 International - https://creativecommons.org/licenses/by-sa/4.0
